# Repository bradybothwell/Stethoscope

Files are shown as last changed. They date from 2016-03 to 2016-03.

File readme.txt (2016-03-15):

GliaX Stethoscope Microphone

Submitted By:	Brady Bothwell, brady@bradybothwell.com
Date:		03/15/2016

Printing Instructions:
Slicer:		slic3r
printer:	mixshop g1 (prusa i3)
Layer Height: 	0.21mm
infill:		35%
support: 	yes

Note: Print Head_Core, with the stethoscope cup pointing up

Bill of Materials:

1 x 2AA Battery Clip
1 x Adafruit Electret Mic Breakout (https://www.adafruit.com/products/1063 - $6.95 US)
1 x Stereo Audio Jack (I used a breakout board from sparkfun but it could be done with any audio jack)

Wire (I use silicone coated wire because its more flexible and less noisy) 
Super Glue
Sticky Tack
Small Rubber Band

Assembly instructions:

See Circuit Layout.pdf for an explanation of the circuit

1. Clear out all support from the prints

2. Solder long leads to the microphone breakout board with the wires protruding from the same side as the mic cylinder

3. Place a bead of glue around the base of the microphone element cylinder

4. Slot the Mic Cylinder into the hole on side of the head, lining up the board with the void provided, the wire should slot into the groove around the outside

5. Place 3 small, even sized blobs of sticky tack on the top of the head

6. Slot the wire through the hole in the head shell

7. Wrap the wire once around the head through the groove, and slip the shell down over the head lining up the hole with the microphone board 

8. press down on the shell to crush the sticky tack and bond it, you could also just use double sided tape

9. Place the rubber band around the groove on the cup side of the head

10. Carefully push the diaphragm over the edge of the cup and rubber band, you can use plastic tools to manipulate the rubber band to avoid cutting it but it doesnt have to be perfect

11. Wire up the wires from the mic to the audio breakout and batteries, see the circuit diagram pdf in the folder

12. Secure the audio breakout into the audio port chassis by gluing the strap arount the two sides of the chassis (check out the 3d models it'll make more sense)

Done!

Note: If the gain is too low, there is a trim pot on the microphone board but it also raises the noise level id probably leave it at halfway

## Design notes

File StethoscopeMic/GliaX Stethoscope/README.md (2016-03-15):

Stethoscope
===========

This project aims to create a research-validated stethoscope whose plans are available freely and openly. The goal is for the bell to cost ~USD$1-2 to produce, and the rest of the stethoscope to cost approximately the same.

Currently, the stethoscope resulting from this project functions as well as the market gold standard, the Littmann Cardiology III.

Bill of Materials
=================

**Printed parts:**
* 1 stethoscope head (head.stl)
* 2 ear tubes (eartube.stl)
* 1 earplug mold (earplug_mold.stl)

**Other hardware:**
Some vendors are suggested. See Bill of materials ODS file for more information.
* 40cm Silicone 12mm OD, 8mm ID
 * [8MM I.D X 12MM O.D NGP60 Clear Transulcent Silicone Hose Pipe Tubing](http://www.advancedfluidsolutions.co.uk/8mm-id-x-12mm-od-clear-transulcent-silicone-hose-pipe-tubing-2480-p.asp) (USD$6.95)

* 20cm UPVC 6mm OD, 4mm ID
 * [Hi-Flex 4mm ID - 6mm OD Flexible PVC Tubing : Clear](http://www.amazon.co.uk/Hi-Flex-4mm-ID-Flexible-Tubing/dp/B004CLLJFS) (USD$11.48)

* Silicone for ear plugs
 * [Moldable Silicone Ear Plugs](http://www.earplugstore.com/moldable-silicone-ear-plugs.html) (USD$1.80)

* Diaphragm: Cut from a report cover with approx 0.35mm plastic sheet
 * [Staples 21639 report cover (UPC 718103160223)](http://www.staples.ca/en/Staples-Swing-Lock-Report-Cover-Clear-with-Black-Spine-5-Pack/product_780953_2-CA_1_20001) (USD$8.84)
 
* Silicone / Rubber ring for diaphram mount

Print Instructions
==================
All printed parts should be printed with PLA plastic at 0.2mm layer height, though it is acceptable for the first layer to be 0.3mm. Infill should be 100%.

Assembly Instructions
=====================
* Insert silicone into mold and allow to set as per manufacturer instructions.
* Attach the diaphragm to the stethoscope head.
* Attach the stethoscope head to the silicone tube.
* Attach the silicone tube to the T-Piece.
* Attach the T-piece to the ear tubes.
* Attach the ear tubes to the molded earplugs.
* Test the stethoscope as per the validation instructions.

Other stethoscopes
==================
Others have made 3D printed stethoscopes too. See:
* https://www.youmagine.com/designs/stethoscope-chestpiece

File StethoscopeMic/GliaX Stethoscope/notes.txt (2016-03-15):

Development notes
-------------------
These are notes/ideas/thoughts about the project that would better fit in a text file than a git commit.

2014-12-02 jglauche - Getting the tube off the head of a Littmann required two flat screwdrivers and some force

2014-12-02 jglauche - I'm not convinced that the stethoscope head alone is responsible for all audio quality. I believe the tubing has to be made so that the earpieces push firmly into the ears, to dampen the noise and to especially transport lower frequencies from the tubing into the ear.

2014-12-02 jglauche - I've created a CrystalSCAD project (ruby to OpenSCAD code) in order to reduce my development time. If this should be a problem later, I might re-write this in pure OpenSCAD code after testing.

2014-12-02 jglauche - I'll start by making a rough sketch of the Littman head

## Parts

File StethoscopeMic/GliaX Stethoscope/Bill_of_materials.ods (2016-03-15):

Quantity | Item | Supplier | Order URL | Price (USD) | Total (USD) | Total(EUR)
1 | 8MM I.D X 12MM O.D NGP60 Clear Transulcent Silicone Hose Pipe Tubing | advancedfluidsolutions.co.uk | http://www.advancedfluidsolutions.co.uk/8mm-id-x-12mm-od-clear-transulcent-silicone-hose-pipe-tubing-2480-p.asp | 6.95 | 6.95 | 6.25 | 0.8992805755
1 | Hi-Flex 4mm ID - 6mm OD Flexible PVC Tubing : Clear | Amazon.co.uk | http://www.amazon.co.uk/Hi-Flex-4mm-ID-Flexible-Tubing/dp/B004CLLJFS | 11.48 | 11.48 | 10.3237410072 | 0.8992805755
1 | Moldable Silicone Ear Plugs | Earplugstore.com | http://www.earplugstore.com/moldable-silicone-ear-plugs.html | 1.8 | 1.8 | 1.618705036 | 0.8992805755
1 | Staples 21639 (UPC 718103160223) Diaphragm | Staples.ca | http://www.staples.ca/en/Staples-Swing-Lock-Report-Cover-Clear-with-Black-Spine-5-Pack/product_780953_2-CA_1_20001 | 8.84 | 8.84 | 7.9496402878 | 0.8992805755
1 | Silicone / Rubber ring for diaphram Mount – Exact Dimensions? | ??? | ??? | ??? | #VALUE! | #VALUE! | 0.8992805755

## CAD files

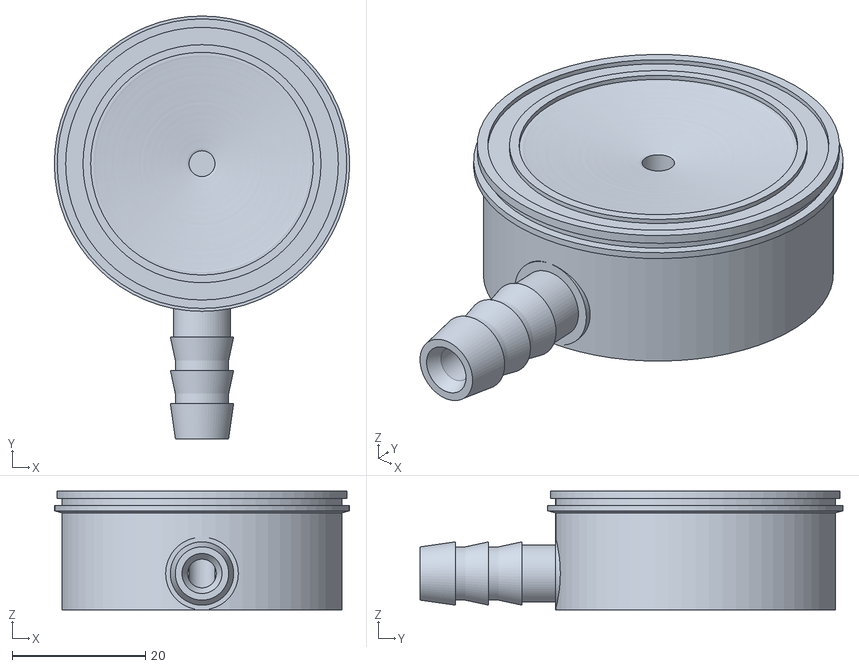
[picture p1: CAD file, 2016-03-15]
StethoscopeMic/GliaX Stethoscope/stethoscope_head/printable_head1.stl
44.3 x 63.4 x 17.8

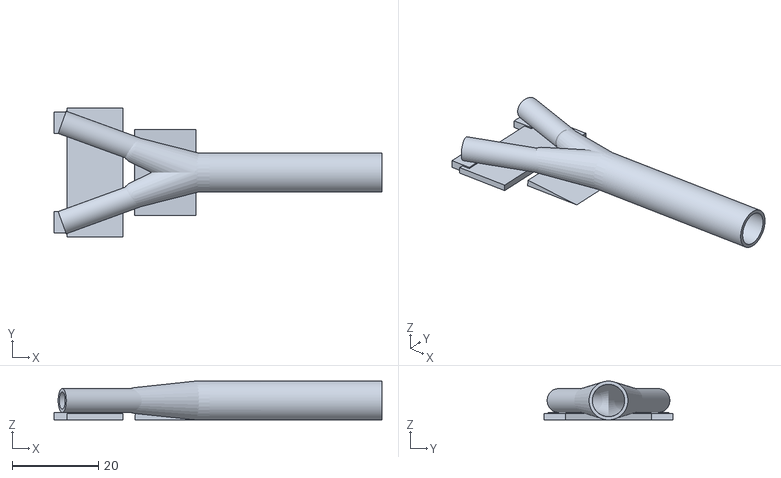
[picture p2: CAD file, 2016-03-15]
StethoscopeMic/GliaX Stethoscope/y_piece.stl
76.0 x 30.0 x 9.00

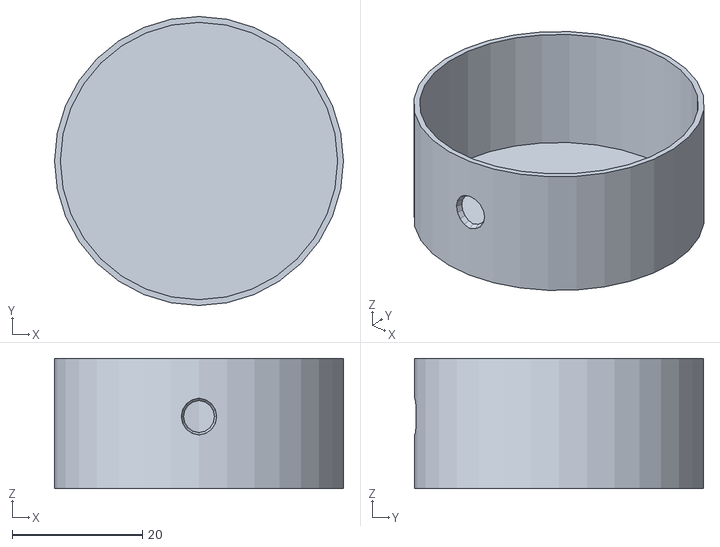
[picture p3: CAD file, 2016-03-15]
StethoscopeMic/Head_Shell.stl
44.3 x 44.3 x 20.0

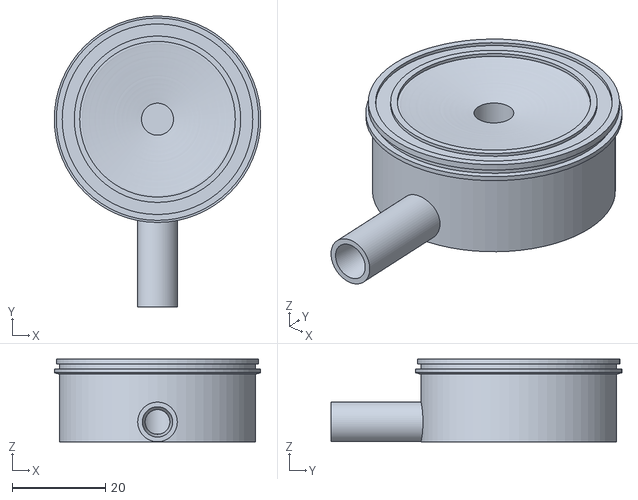
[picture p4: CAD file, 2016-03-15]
StethoscopeMic/GliaX Stethoscope/head.stl
44.3 x 62.4 x 17.8

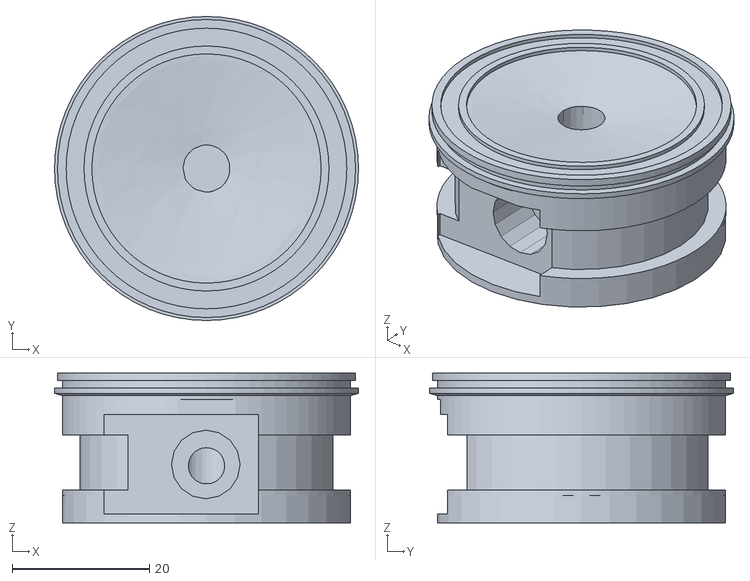
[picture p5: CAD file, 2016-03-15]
StethoscopeMic/Head_Core.stl
44.3 x 44.3 x 21.8

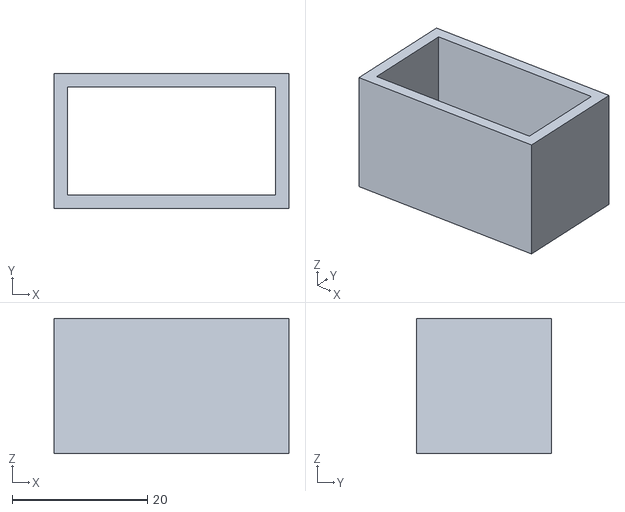
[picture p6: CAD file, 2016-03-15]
StethoscopeMic/Audio_Port_Chassis_Strap.stl
34.8 x 20.0 x 20.0

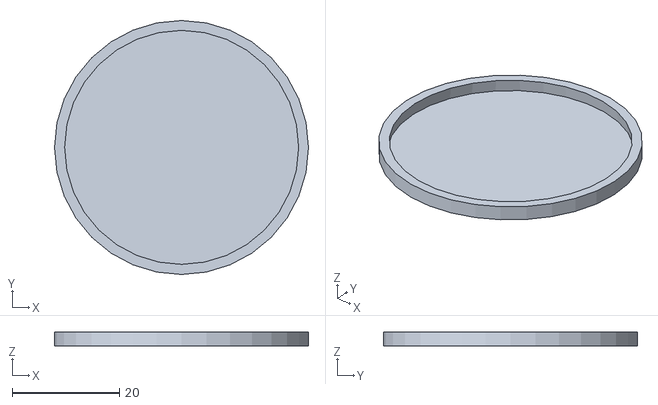
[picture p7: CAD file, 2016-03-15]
StethoscopeMic/Diaphragm.stl
47.5 x 47.5 x 2.70

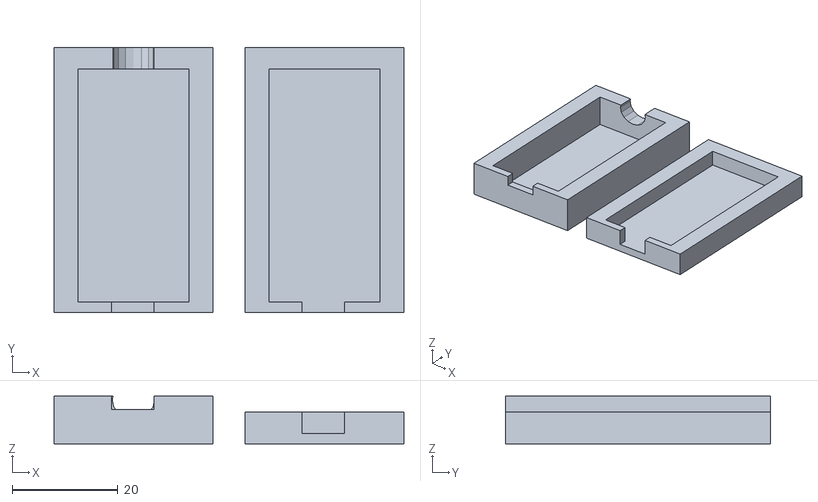
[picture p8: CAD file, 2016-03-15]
StethoscopeMic/Audio_Port_Housing.stl
66.1 x 50.0 x 9.00

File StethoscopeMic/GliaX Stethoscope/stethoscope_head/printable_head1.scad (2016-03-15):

$fn=64;
union(){translate(v = [0, 0, 17.800])
mirror(v = [0, 0, 1])
difference(){union(){intersection(){translate(v = [-50.000, -50.000])
cube(size = [100, 100, 17.800]);
union(){union(){union(){union(){union(){union(){union(){union(){union(){cylinder(h = 1.080, r = 21.715);
translate(v = [0, 0, 1.080])
cylinder(h = 1.060, r = 21.000);
}
translate(v = [0, 0, 2.140])
cylinder(h = 0.800, r = 22.150);
}
translate(v = [0, 0, 2.940])
cylinder(h = 3.260, r1 = 22.150, r2 = 10.500);
}
translate(v = [0, 0, 6.200])
cylinder(h = 1.300, r1 = 10.500, r2 = 8.475);
}
translate(v = [0, 0, 7.500])
cylinder(h = 13.500, r1 = 8.475, r2 = 13.500);
}
translate(v = [0, 0, 21.000])
cylinder(h = 4.000, r1 = 13.500, r2 = 16.375);
}
translate(v = [0, 0, 25.000])
cylinder(h = 0.800, r = 15.500);
}
translate(v = [0, 0, 25.800])
cylinder(h = 1.420, r = 17.215);
}
translate(v = [0, 0, 13.500])
rotate(a = [90, 0, 0])
difference(){union(){cylinder(h = 20, r = 5.450);
translate(v = [0, 0, 20])
difference(){union(){union(){cylinder(h = 20.300, r = 4.250);
cylinder(h = 5, r = 4.500);
}
translate(v = [0, 0, 5])
union(){union(){cylinder(h = 3.500, r1 = 4.750, r2 = 4.250);
translate(v = [0, 0, 5.000])
cylinder(h = 3.500, r1 = 4.750, r2 = 4.250);
}
translate(v = [0, 0, 10.000])
cylinder(h = 5.200, r1 = 4.750, r2 = 4.250);
}
}
translate(v = [0, 0, 13.800])
union(){cylinder(h = 6.500, r1 = 2.500, r2 = 3.250);
translate(v = [0, 0, 6.500])
cylinder(h = 1, r = 3.250);
}
}
}
translate(v = [0, 0, -0.010])
cylinder(h = 40.320, r = 2.650);
}
}
}
cylinder(h = 17.800, r = 21.000);
}
union(){union(){union(){translate(v = [0, 0, -0.010])
difference(){cylinder(h = 0.570, r = 20.450);
translate(v = [0, 0, -0.010])
cylinder(h = 0.590, r = 17.850);
}
translate(v = [0, 0, 0.560])
union(){translate(v = [0, 0, 2.735])
mirror(v = [0, 0, 1])
rotate_extrude(convexity = 10){polygon(points = [[0.000, 0], [0.250, 0], [0.500, 0], [0.750, 0], [1.000, 0], [1.250, 0.160], [1.500, 0.460], [1.750, 0.720], [2.000, 0.850], [2.250, 0.930], [2.500, 0.960], [2.750, 0.990], [3.000, 1.020], [3.250, 1.050], [3.500, 1.085], [3.750, 1.120], [4.000, 1.150], [4.250, 1.180], [4.500, 1.215], [4.750, 1.248], [5.000, 1.278], [5.250, 1.308], [5.500, 1.340], [5.750, 1.372], [6.000, 1.401], [6.250, 1.432], [6.500, 1.465], [6.750, 1.500], [7.000, 1.529], [7.250, 1.559], [7.500, 1.593], [7.750, 1.630], [8.000, 1.659], [8.250, 1.690], [8.500, 1.723], [8.750, 1.760], [9.000, 1.788], [9.250, 1.811], [9.500, 1.849], [9.750, 1.880], [10.000, 1.910], [10.250, 1.940], [10.500, 1.973], [10.750, 2.005], [11.000, 2.035], [11.250, 2.065], [11.500, 2.100], [11.750, 2.134], [12.000, 2.168], [12.250, 2.199], [12.500, 2.230], [12.750, 2.263], [13.000, 2.291], [13.250, 2.320], [13.500, 2.358], [13.750, 2.390], [14.000, 2.420], [14.250, 2.450], [14.500, 2.480], [14.750, 2.518], [15.000, 2.548], [15.250, 2.578], [15.500, 2.613], [15.750, 2.648], [16.000, 2.680], [16.250, 2.735], [16.700, 2.735], [0, 2.735]]);
}
translate(v = [0, 0, -2])
cylinder(h = 2, r = 16.700);
}
}
translate(v = [0, 0, 13.500])
rotate(a = [90, 0, 0])
translate(v = [0, 0, -0.010])
cylinder(h = 40.320, r = 2.650);
}
translate(v = [0, 0, -0.010])
cylinder(h = 27.240, r = 3.440);
}
}
cylinder(h = 1.700, r = 5.000);
}

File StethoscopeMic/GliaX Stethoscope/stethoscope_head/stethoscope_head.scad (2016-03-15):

$fn=64;
color("lightgrey"){difference(){union(){union(){union(){union(){union(){union(){union(){union(){union(){cylinder(h = 1.080, r = 21.715);
translate(v = [0, 0, 1.080])
cylinder(h = 1.060, r = 21.000);
}
translate(v = [0, 0, 2.140])
cylinder(h = 0.800, r = 22.150);
}
translate(v = [0, 0, 2.940])
cylinder(h = 3.260, r1 = 22.150, r2 = 10.500);
}
translate(v = [0, 0, 6.200])
cylinder(h = 1.300, r1 = 10.500, r2 = 8.475);
}
translate(v = [0, 0, 7.500])
cylinder(h = 13.500, r1 = 8.475, r2 = 13.500);
}
translate(v = [0, 0, 21.000])
cylinder(h = 4.000, r1 = 13.500, r2 = 16.375);
}
translate(v = [0, 0, 25.000])
cylinder(h = 0.800, r = 15.500);
}
translate(v = [0, 0, 25.800])
cylinder(h = 1.420, r = 17.215);
}
translate(v = [0, 0, 12.350])
rotate(a = [90, 0, 0])
difference(){union(){cylinder(h = 21, r = 5.450);
translate(v = [0, 0, 21])
difference(){union(){union(){cylinder(h = 20.300, r = 4.000);
cylinder(h = 5, r = 4.250);
}
translate(v = [0, 0, 5])
union(){union(){cylinder(h = 3.500, r1 = 4.750, r2 = 4.000);
translate(v = [0, 0, 5.000])
cylinder(h = 3.500, r1 = 4.750, r2 = 4.000);
}
translate(v = [0, 0, 10.000])
cylinder(h = 5.200, r1 = 4.750, r2 = 4.000);
}
}
translate(v = [0, 0, 18.300])
union(){cylinder(h = 2.000, r1 = 2.000, r2 = 3.000);
translate(v = [0, 0, 2.000])
cylinder(h = 1, r = 3.000);
}
}
}
translate(v = [0, 0, -0.010])
cylinder(h = 41.320, r = 2.000);
}
}
union(){union(){union(){translate(v = [0, 0, -0.010])
difference(){cylinder(h = 0.570, r = 20.450);
translate(v = [0, 0, -0.010])
cylinder(h = 0.590, r = 17.850);
}
translate(v = [0, 0, 0.560])
union(){translate(v = [0, 0, 2.735])
mirror(v = [0, 0, 1])
rotate_extrude(convexity = 10){polygon(points = [[0.000, 0], [0.250, 0], [0.500, 0], [0.750, 0], [1.000, 0], [1.250, 0.160], [1.500, 0.460], [1.750, 0.720], [2.000, 0.850], [2.250, 0.930], [2.500, 0.960], [2.750, 0.990], [3.000, 1.020], [3.250, 1.050], [3.500, 1.085], [3.750, 1.120], [4.000, 1.150], [4.250, 1.180], [4.500, 1.215], [4.750, 1.248], [5.000, 1.278], [5.250, 1.308], [5.500, 1.340], [5.750, 1.372], [6.000, 1.401], [6.250, 1.432], [6.500, 1.465], [6.750, 1.500], [7.000, 1.529], [7.250, 1.559], [7.500, 1.593], [7.750, 1.630], [8.000, 1.659], [8.250, 1.690], [8.500, 1.723], [8.750, 1.760], [9.000, 1.788], [9.250, 1.811], [9.500, 1.849], [9.750, 1.880], [10.000, 1.910], [10.250, 1.940], [10.500, 1.973], [10.750, 2.005], [11.000, 2.035], [11.250, 2.065], [11.500, 2.100], [11.750, 2.134], [12.000, 2.168], [12.250, 2.199], [12.500, 2.230], [12.750, 2.263], [13.000, 2.291], [13.250, 2.320], [13.500, 2.358], [13.750, 2.390], [14.000, 2.420], [14.250, 2.450], [14.500, 2.480], [14.750, 2.518], [15.000, 2.548], [15.250, 2.578], [15.500, 2.613], [15.750, 2.648], [16.000, 2.680], [16.250, 2.735], [16.700, 2.735], [0, 2.735]]);
}
translate(v = [0, 0, -2])
cylinder(h = 2, r = 16.700);
}
}
translate(v = [0, 0, 12.350])
rotate(a = [90, 0, 0])
translate(v = [0, 0, -0.010])
cylinder(h = 41.320, r = 2.000);
}
translate(v = [0, 0, -0.010])
cylinder(h = 27.240, r = 1.575);
}
}
}

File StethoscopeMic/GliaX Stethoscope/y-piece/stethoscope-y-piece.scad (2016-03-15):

//change2
module tube(id,od,l){
   difference(){
    cylinder(r=od/2,l,$fn=100,center=true);
    translate([0,0,-1])cylinder(r=id/2,l+2,$fn=100,center=true);
    
   }
    
    
}

module channel(){
	for(i=[-20,20])rotate([0,0,i]){
		hull(){
			sphere(7.5/2,$fn=30);
			translate([10,0,0])sphere(4.5/2,$fn=30);
		}
		hull(){
			translate([10,0,0])sphere(4.5/2,$fn=30);
			translate([20,0,0])sphere(4/2,$fn=30);
		}
	}
	translate([-7.5,0,0])rotate([0,90,0])cylinder(r=7.5/2,h=15,$fn=30,center=true);
}

module shell(){
	for(i=[-20,20])rotate([0,0,i]){
		hull(){
			sphere(9/2,$fn=30);
			translate([15,0,0])sphere(6/2,$fn=30);
		}

	}
	translate([-7.5,0,0])rotate([0,90,0])cylinder(r=9/2,h=15,$fn=30,center=true);
}



translate([0,0,4.5])render()difference(){
union(){translate([0,0,0])mirror()shell();
translate([-17,8.50,0])rotate(a=90,v=[0,1,0]){
translate([0,-2,0])rotate(a=20,v=[1,0,0])tube(4,5.5,30);
translate([0,-15,0])rotate(a=20,v=[-1,0,0])tube(4,5.5,30);
translate([0,-8.5,40])tube(7.5,9,40);
}
}
translate([0,0,0])mirror()channel();
}
%cube([200,200,0.01],center=true);

#translate([2.8,0,0]){rotate(a=180,v=[0,0,1])
difference(){
    
rotate(a=6,v=[0,-1,0]){
translate([7,0,-5.3]){
cube ([20,20,10],center=true);}}
translate([0,0,-5])    cube ([70,70,10],center=true);
translate([0,0,-8])    cube ([70,70,10],center=true);
}}
translate([-33,9,0])cube([5,5,1.75]);
translate([-33,-14,0])cube([5,5,1.75]);
translate([-30,-15,0])cube([13,30,1.45]);
	
	

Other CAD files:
StethoscopeMic/GliaX Stethoscope/stethoscope_head/printable_head2.stl

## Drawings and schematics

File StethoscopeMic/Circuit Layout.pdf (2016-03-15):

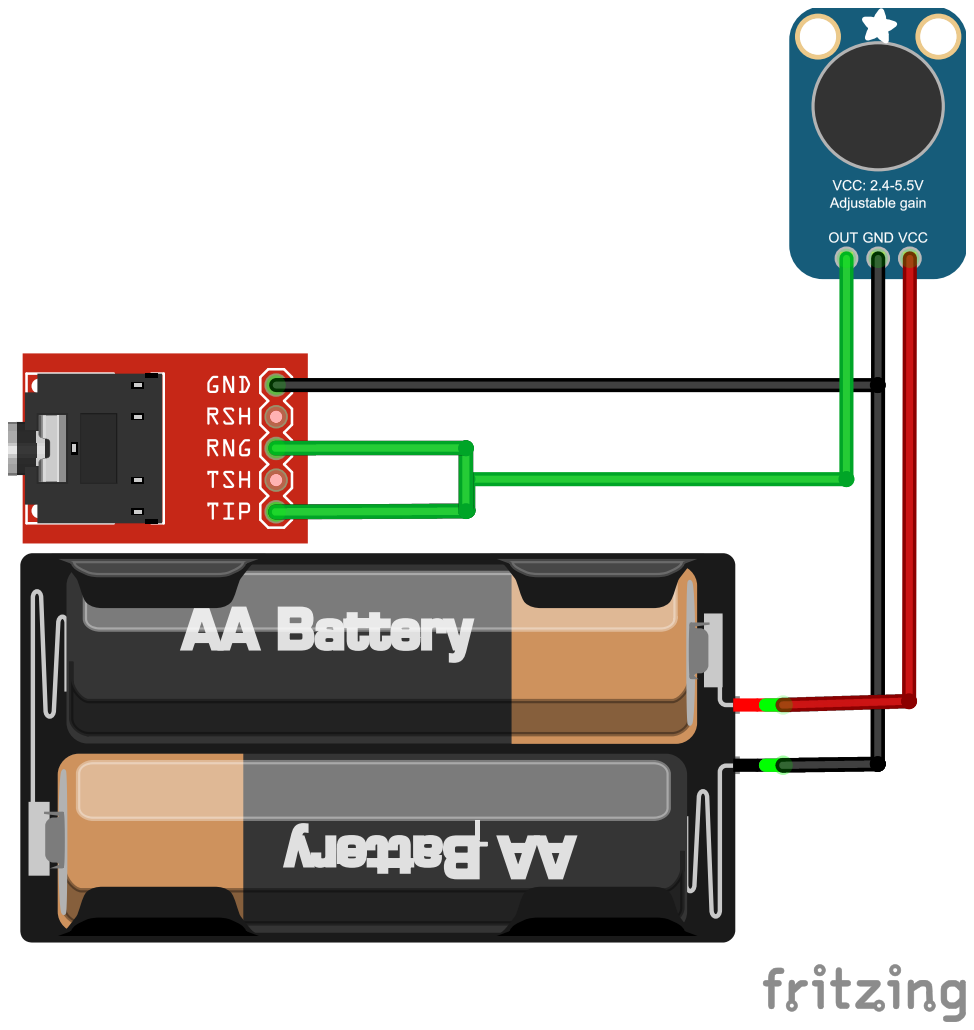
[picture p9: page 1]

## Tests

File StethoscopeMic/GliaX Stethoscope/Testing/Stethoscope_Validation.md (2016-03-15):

#Glia Stethoscope Validation Procedure
---
##Ideology
A stethoscope is a fundamental medical tool used by doctors worldwide to characterize heart and lung sounds. A spectral analysis of heart sounds has shown the frequencies of interest are 0-500Hz [1]. Similar analysis of respiratory sounds has shown the frequencies of interest are 0-2000Hz [2]. A stethoscope that can reliably transmit frequencies at these levels has the greatest potential to be diagnostically useful.

##Setup
There are many different stethoscope models made by numerous companies which each claim to have a superior product. Previous work by *Abella et al* objectively tested the acoustic properties of 6 different models by measuring the power spectrum of frequencies ranging from 37.5-1000 Hz to determine which stethoscope was most efficient at transmitting sound [3]. At the time of this testing (1992) the Littmann Cardiology II was found to have superior qualities.

More recently in 2008 *Finkelstein* expanded this evaluation to include a subjective component by having a group of clinicians use each model on numerous patients and rate the clarity and loudness of sound transduction. Coupling this rating with subjective data at this time it was found that the Littmann Cardiology III was the best device on the market [4].

The frequency response of various Glia Model stethoscopes was determined using an experimental setup modelled off of the one used by *Watrous, Grove and Bowen* [5] shown below.

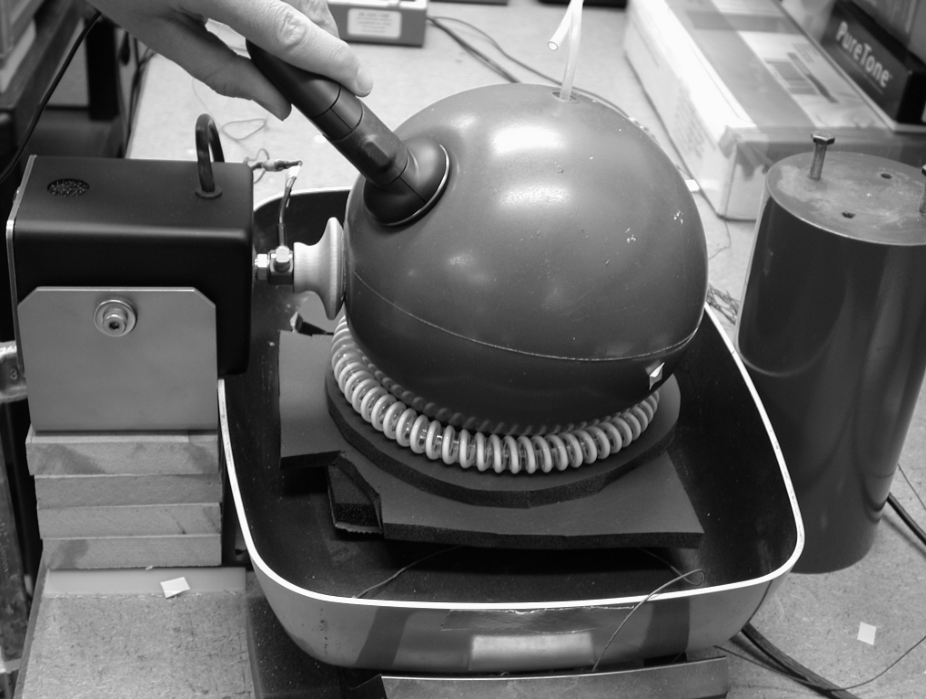
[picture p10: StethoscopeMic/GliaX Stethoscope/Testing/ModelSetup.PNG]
Approximate Test Setup


In the above topology, the balloon contains 2L of water (2000g), acoustic input is supplied via a pair of Monster DNA headphones and sounds were recorded using a Hama microphone. Audacity was used to create a 15 second audio clip of white noise which was played through the setup with the output of each stethoscope being recorded for spectral analysis. The spectrum produced by each stethoscope model was then compared to that of the Littmann Cardiology III. These plots are shown below     

##Results
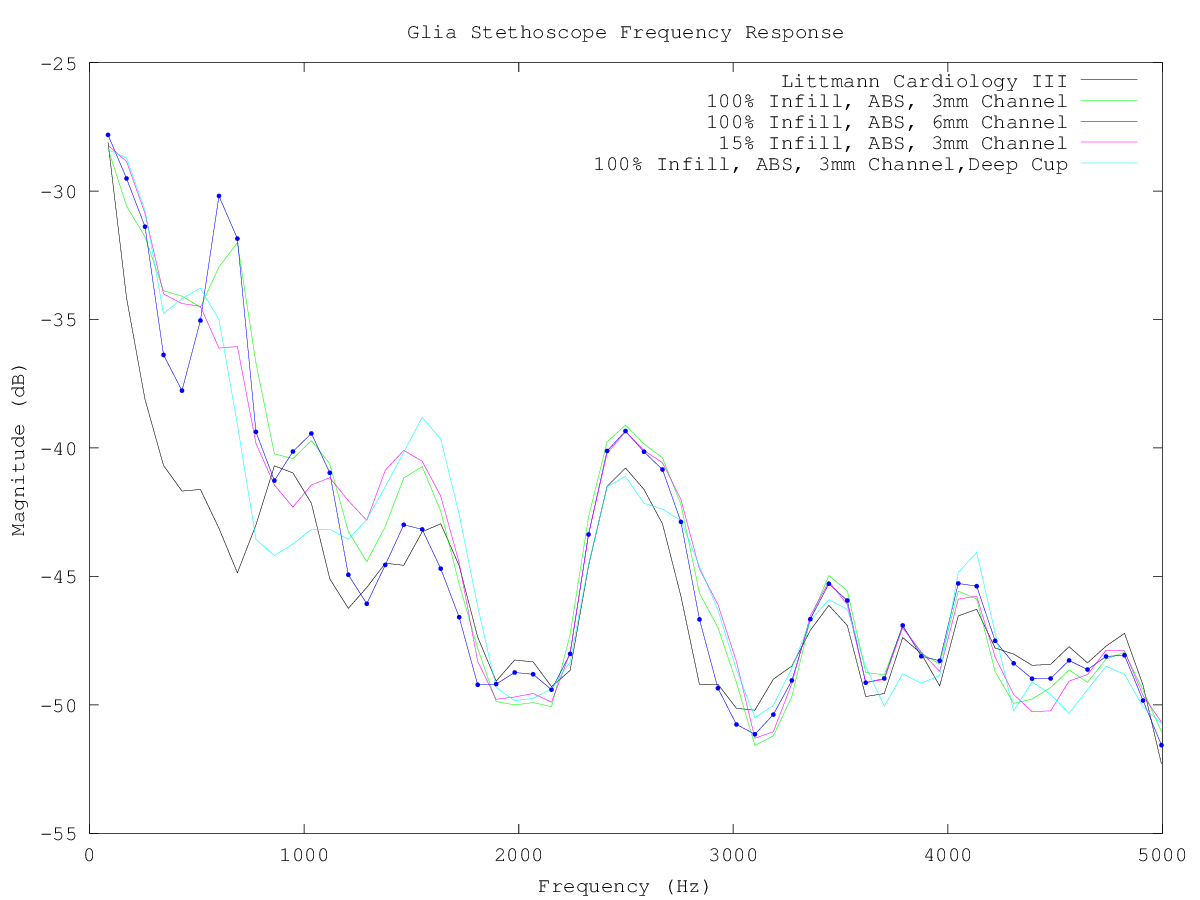
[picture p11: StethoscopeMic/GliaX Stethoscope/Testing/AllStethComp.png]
All Stethoscope Heads

---
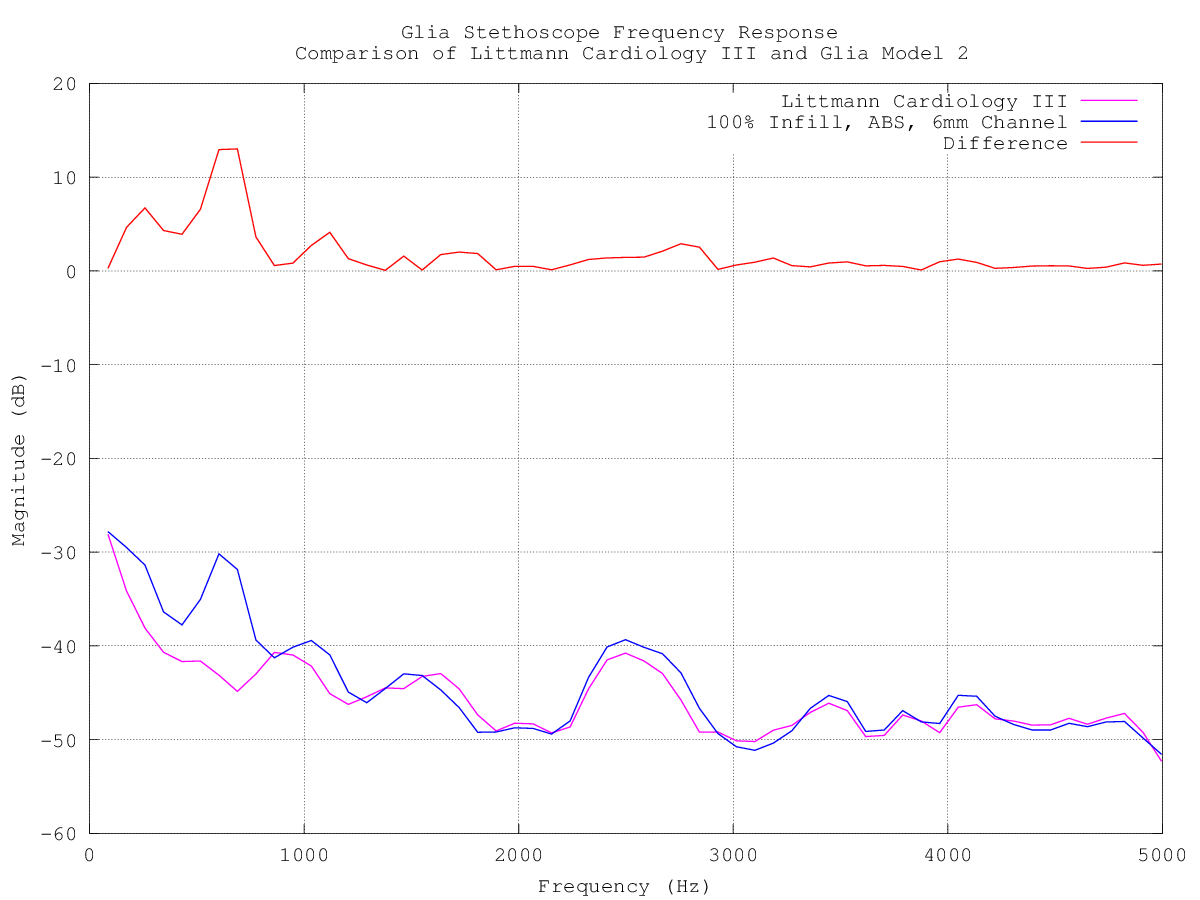
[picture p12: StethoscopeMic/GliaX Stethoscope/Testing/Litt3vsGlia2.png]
Glia 2 Vs. Littmann Cardiology III


##References 
[1] Rushmer, R.F. *Cardiovascular Dynamics 4th Edition* 1976 WB Saunders

[2]Pasterkamp H, Kraman S, Wodicka G. *Respiratory sounds. Advances beyond the stethoscope*. Am J RespirfckLRCrit Care Med 1997, 156: 974–987. 

[3] - Abella M, Formolo J, Penney DG. *Comparison of the acoustic properties of six popular stethoscopes* J Acoust Soc Am 1992 Apr;91(4 Pt 1):2224-2228

[4] - Finkelstein,E. *The Ultimate Acoustic Stethoscope Review* For Us Docs : The Consumer Magazine for Doctors [Online] available from : 
[http://www.forusdocs.com/reviews/Acoustic_Stethoscope_Review.htm](http://www.forusdocs.com/reviews/Acoustic_Stethoscope_Review.htm)
                           
[5] Watrous, RL. Grove, DM. Bowen, DL. *"Methods and Results in Characterizing Electronic Stethoscopes"* Computers in Cardiology 2002;29:653-656

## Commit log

2016-03-15 Added files via upload
    A prototype of a Stethoscope Microphone which uses the GliaX Head at its core
    [Audio_Port_Chassis_Strap.stl, Audio_Port_Housing.stl, Diaphragm.stl, Head_Core.stl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]
2016-03-15 Placed root model in its own directory
    [Audio_Port_Chassis_Strap.stl, Audio_Port_Housing.stl, Bill_of_materials.ods, Diaphragm.stl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]
